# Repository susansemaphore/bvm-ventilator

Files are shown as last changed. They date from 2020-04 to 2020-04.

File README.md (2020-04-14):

# ResQ̇V̇enT Ventilator
An open-source Bag Valve Mask (BVM) based ventilator. Designed to be simple, low cost and robust. The project aims to assist hospitals, by supplementing their existing ventilator fleet in times of high demand such as the COVID-19 outbreak.

## System Diagram
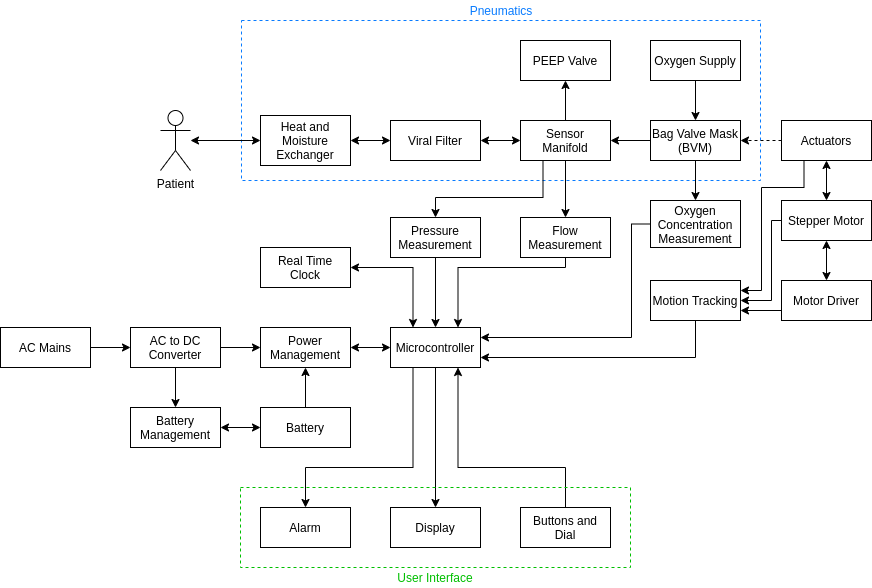
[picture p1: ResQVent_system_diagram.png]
ResQ̇V̇enT System Diagram


## Requirements
### Primary Technical Requirements
* Working pressure at patient: 10 - 40 HPa
* Tidal Volume: 250 - 800 ml
* Respiratory Rate: 10 - 30 cycles/min
* I:E ratio variable between 1:1 - 1:3
* Physical peak pressure relief: Fixed at 40 HPa
* Adjustable PEEP pressure
* All adjustable parameters should be adjustable without interrupting operation
* Infection control
  * All components that come into contact with the patient’s breath need to be easily cleaned or disposable
  * The working pressure should accommodate the use of a HMEF-bacterial-viral filter
* Reliability: 100% duty cycle for 14 days
* Safety: The device should not pose any risk to the patient or healthcare workers
* Mode of operation: Mandatory Ventilation - Fixed timing parameters with no external breath triggers

### Secondary Technical Requirements
* Mode of operation: Pressure support - The patient initiates a breath which is supported by the machine.
* Accommodation for an ultrasonic humidifier-warmer
* Battery backup - the minimum period of which needs to comfortably span the time it may take for a backup generator to kick in. However longer term operation would be ideal

### User Requirements
* The device as a whole needs to be easily cleanable
* Information display needs to be clear
* User interaction needs to be obvious and in metrics commonly understood by doctors
* User manual to be simple 1 pager
* The BVM should be easily replaceable and the machine's recalibration should be simple

### Other Requirements
* Cost: As low as possible. But being a medical device, robustness and feature completion is the primary goal.

## Requirements source documents
* [SASA Ventilator Requirements](https://drive.google.com/file/d/1E5HM6Y5oINCTi7c1G11EO2v6UM-miFut/view?usp=sharing)
* [UK Government Ventilator Requirements ](https://www.gov.uk/government/publications/coronavirus-covid-19-ventilator-supply-specification/rapidly-manufactured-ventilator-system-specification)
* [Open source requirements](https://docs.google.com/document/d/1FNPwrQjB1qW1330s5-S_-VB0vDHajMWKieJRjINCNeE/edit?fbclid=IwAR3ugu1SGMsacwKi6ycAKJFOMduInSO4WVM8rgmC4CgMJY6cKaGBNR14mpM)

## Similar Projects
* [OpenLung](https://gitlab.com/TrevorSmale/OSV-OpenLung/-/tree/master)
* [Open Source Covid-19 Ventilator Canada](https://open-source-covid-19-ventilator-canada.mn.co/)
* [E-Vent - MIT](https://e-vent.mit.edu/)
* [COVID-19 Project: Rapidly Manufactured Medical Equipment - OfferZen](https://www.offerzen.com/blog/covid-19-project-rapidly-manufactured-medical-equipment)
* [ApolloBVM by Take a Breather - Rice University](https://news.rice.edu/2020/03/27/ventilator-costing-less-than-300-developed-by-rice-university-and-metric-technologies/)
* [Ambovent](https://github.com/AmboVent/AmboVent)

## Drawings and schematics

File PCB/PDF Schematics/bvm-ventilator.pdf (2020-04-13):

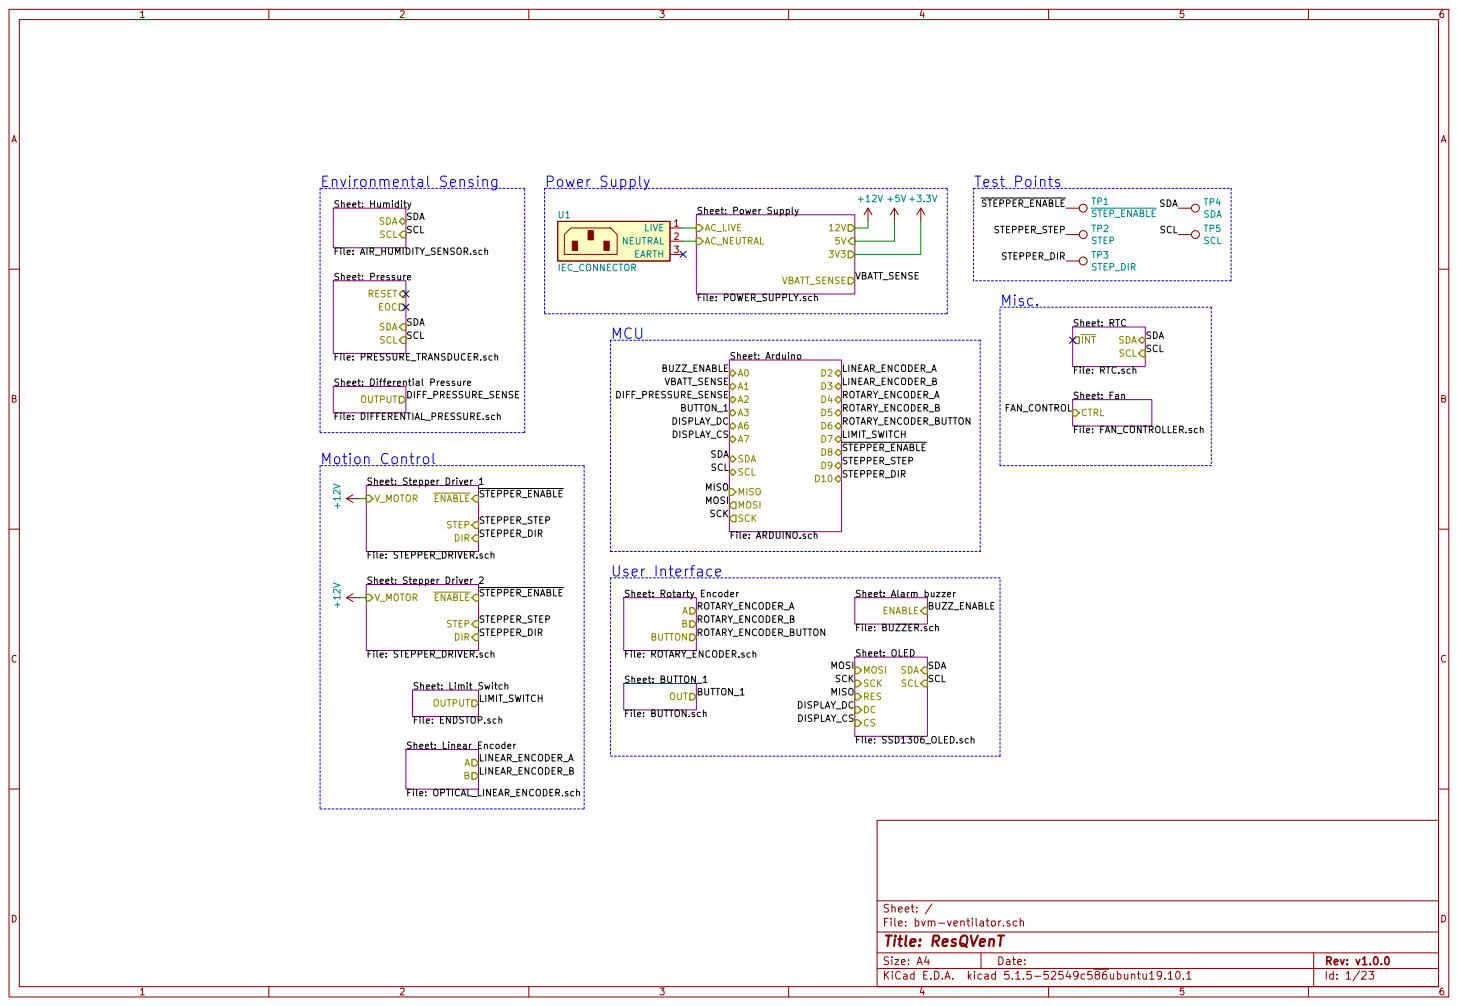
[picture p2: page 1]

TP1 STEP_ENABLE +12V
Sheet: Humidity File: AIR_HUMIDITY_SENSOR.sch SDA

Sheet: Fan File: FAN_CONTROLLER.sch CTRL +12V

INT Sheet: Power Supply File: POWER_SUPPLY.sch AC_LIVE

IEC_CONNECTOR +12V
Sheet: Pressure File: PRESSURE_TRANSDUCER.sch RESET EOC

DISPLAY_DC
DISPLAY_CS MISO MOSI SCK
SCL SDA ROTARY_ENCODER_B
SCL MISO MOSI SCK

Sheet: Stepper Driver 1 File: STEPPER_DRIVER.sch V_MOTOR

Sheet: Stepper Driver 2 File: STEPPER_DRIVER.sch V_MOTOR

Sheet: BUTTON_1 File: BUTTON.sch OUT Sheet: Rotarty Encoder File: ROTARY_ENCODER.sch A

Sheet: Alarm buzzer File: BUZZER.sch ENABLE

Sheet: Linear Encoder File: OPTICAL_LINEAR_ENCODER.sch A

File: bvm-ventilator.sch Sheet: /
Id: 1/23 Title: ResQVenT

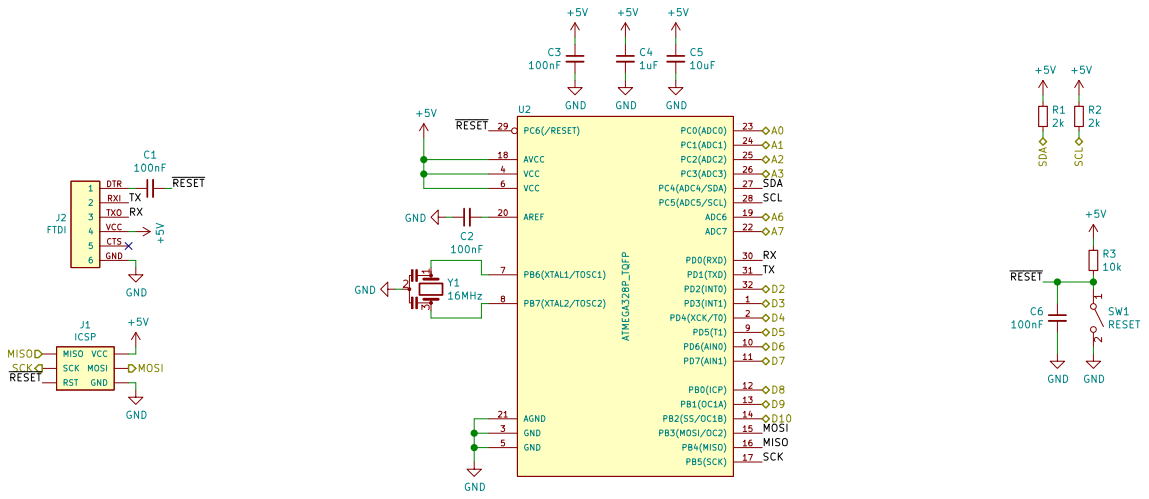
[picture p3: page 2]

File: ARDUINO.sch Sheet: /Arduino/
Id: 2/23 Title: ResQVenT

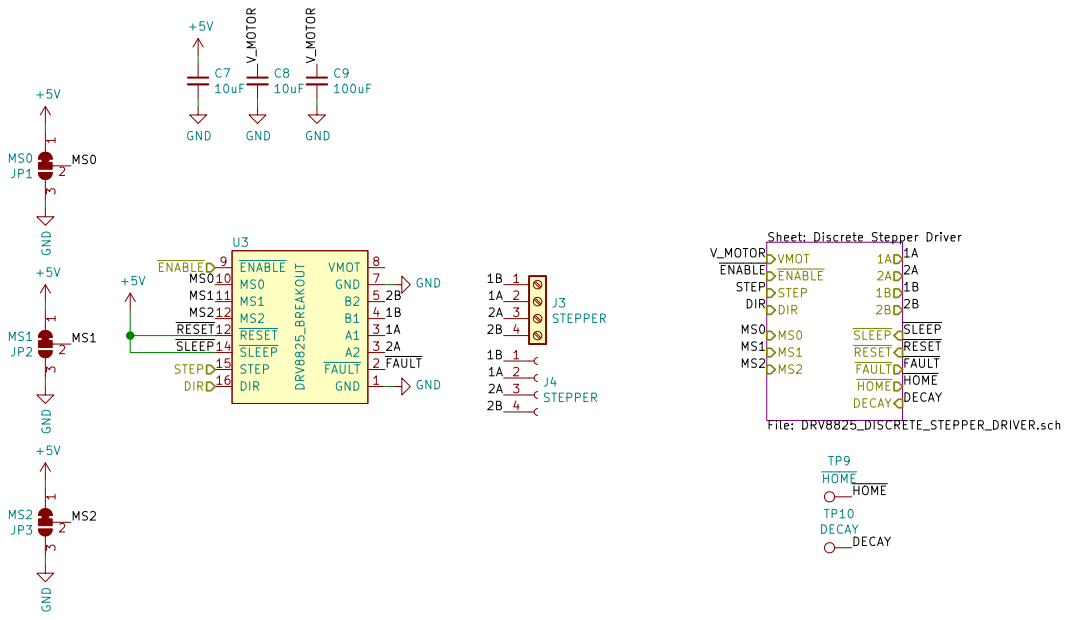
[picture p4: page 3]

FAULT HOME DECAY GND GND

Sheet: Discrete Stepper Driver File: DRV8825_DISCRETE_STEPPER_DRIVER.sch

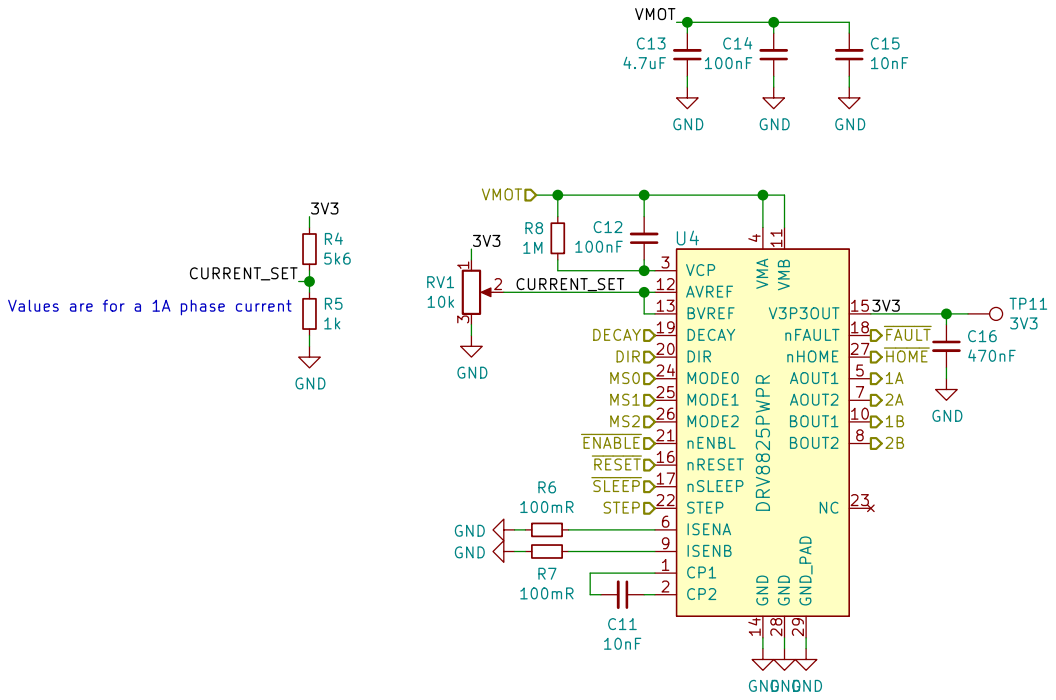
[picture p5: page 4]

3V3 CURRENT_SET Values are for a 1A phase current

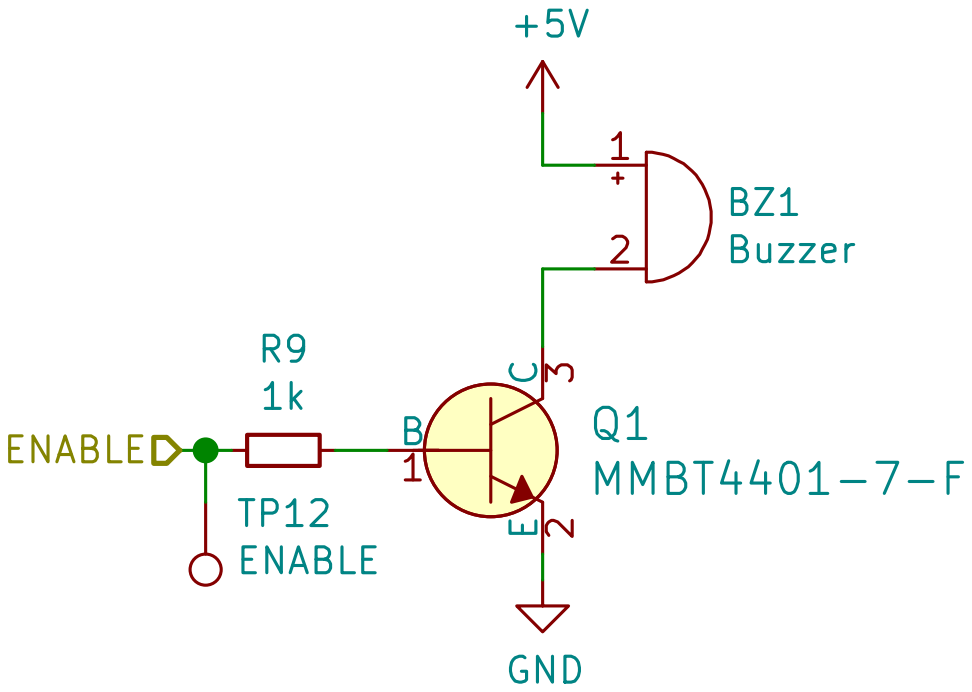
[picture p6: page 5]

File: BUZZER.sch Sheet: /Alarm buzzer/ B

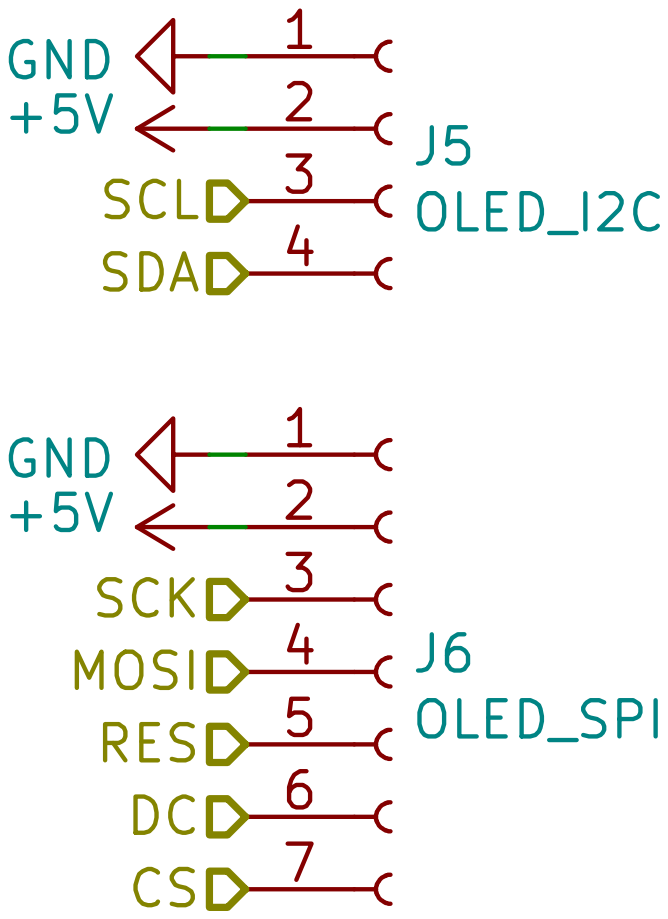
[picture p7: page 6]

File: SSD1306_OLED.sch Sheet: /OLED/ GND
J6OLED_SPI +5V

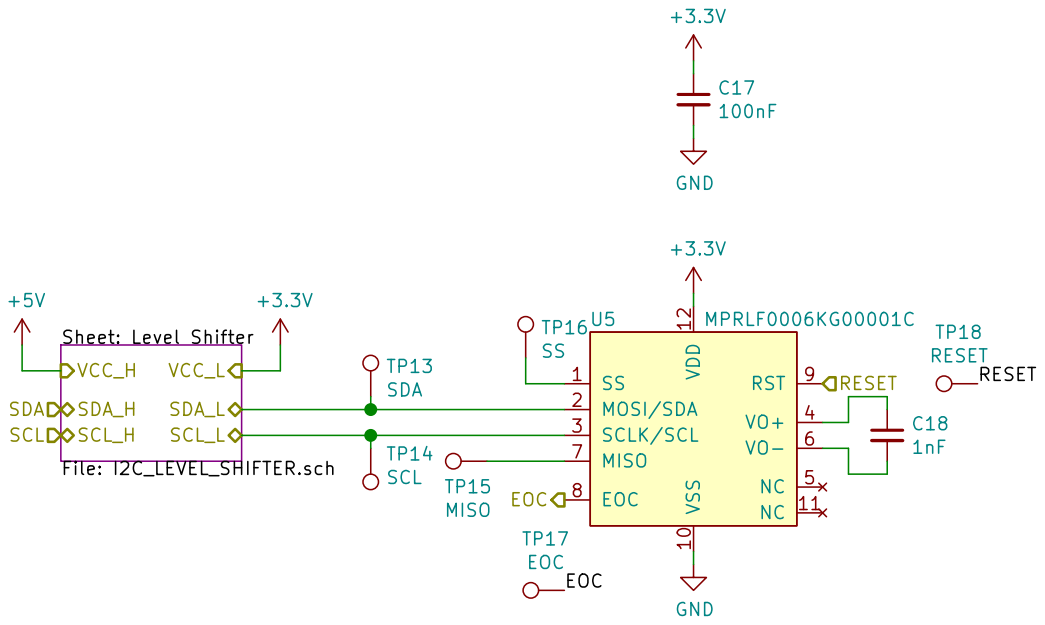
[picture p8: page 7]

TP14 SCL +5V
Sheet: Level Shifter File: I2C_LEVEL_SHIFTER.sch SDA_L SCL_L SDA_H

File: PRESSURE_TRANSDUCER.sch Sheet: /Pressure/
Id: 7/23 Title: ResQVenT

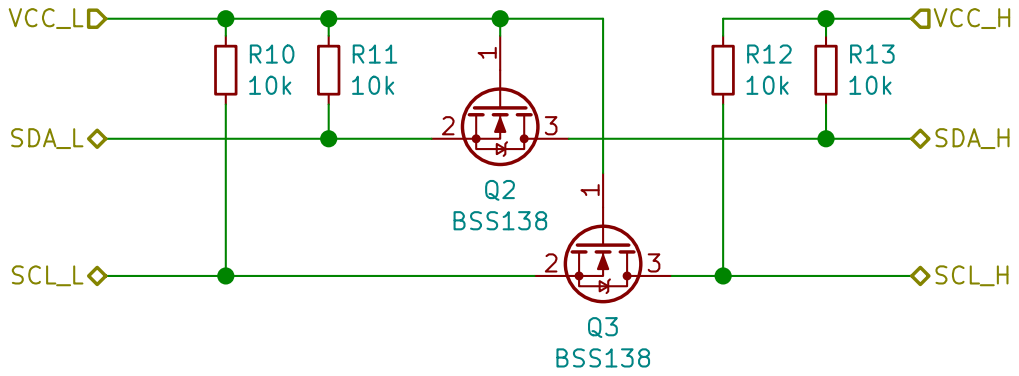
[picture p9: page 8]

File: I2C_LEVEL_SHIFTER.sch Sheet: /Pressure/Level Shifter/
Id: 8/23 Title: ResQVenT

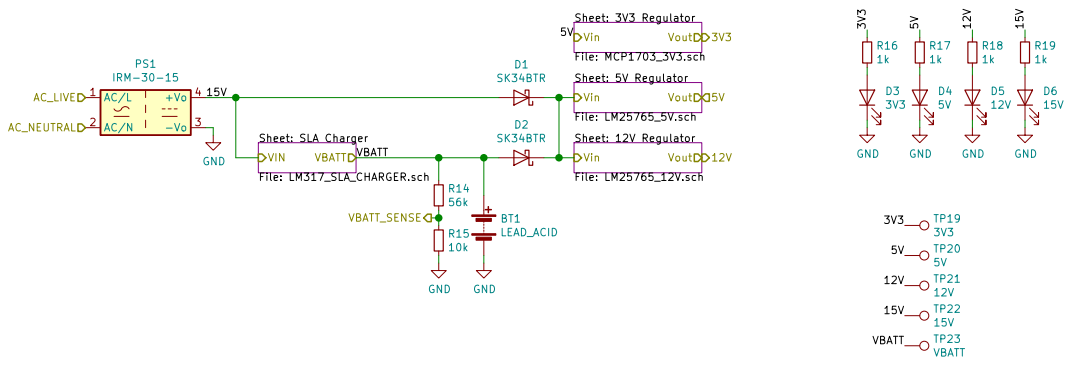
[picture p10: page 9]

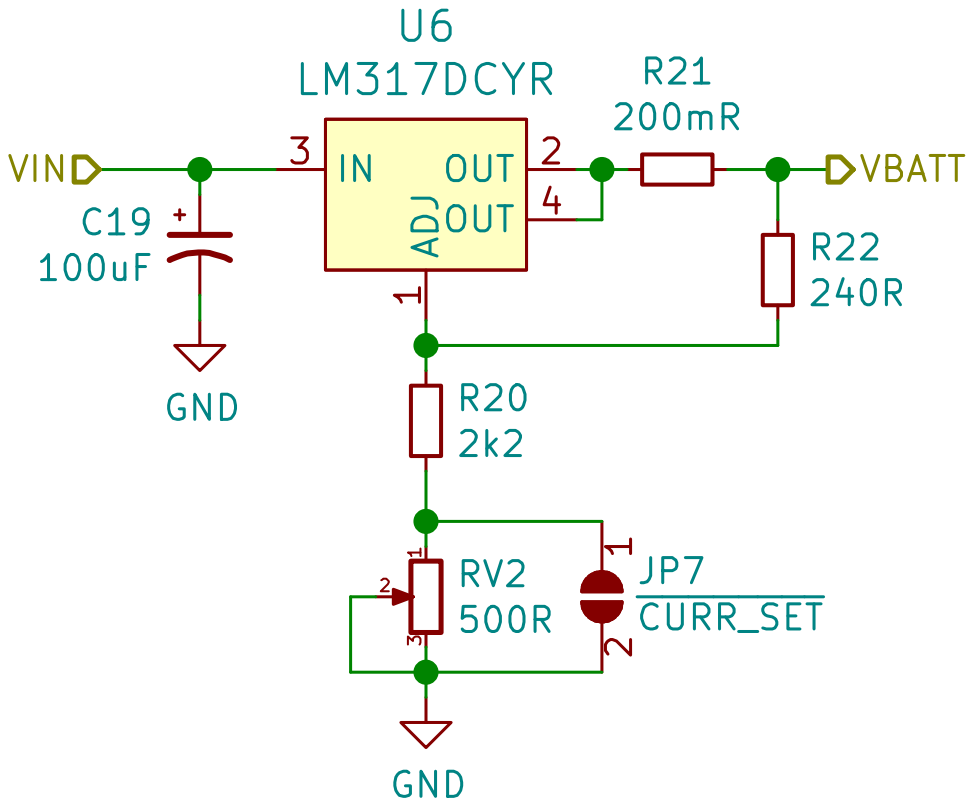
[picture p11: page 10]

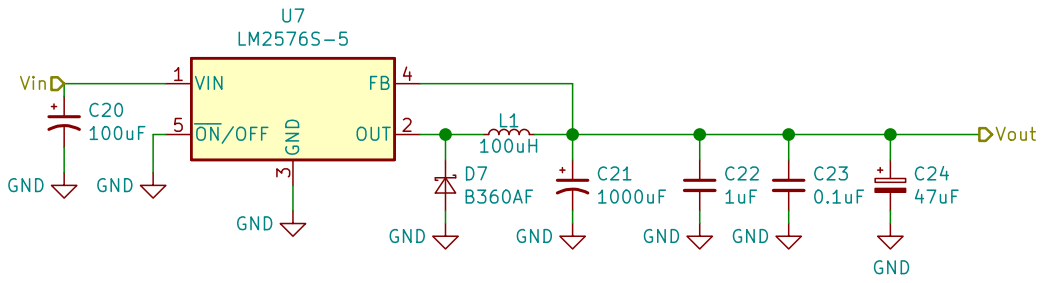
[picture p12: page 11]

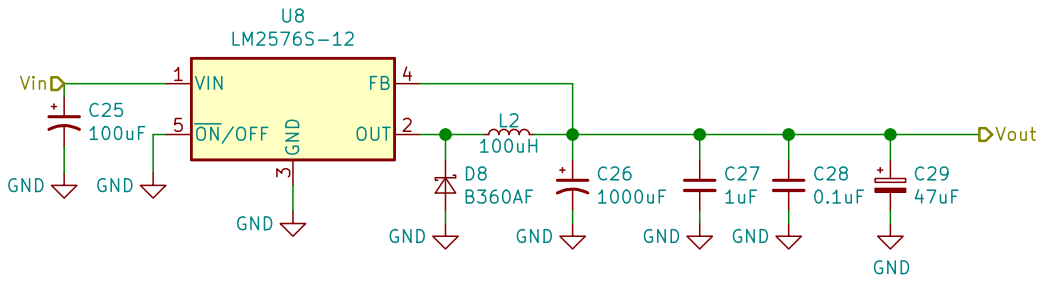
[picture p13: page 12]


1 VO 2 VI 3 U9 MCP1703A-3302_SOT23 Vin Vout

Sheet: /Power Supply/3V3 Regulator/ C30


FAULT HOME DECAY GND GND

Sheet: Discrete Stepper Driver File: DRV8825_DISCRETE_STEPPER_DRIVER.sch


3V3 CURRENT_SET Values are for a 1A phase current


File: RTC.sch Sheet: /RTC/ BT2 C2032 +5V


File: ENDSTOP.sch Sheet: /Limit Switch/
Id: 17/23 Title: ResQVenT



File: BUTTON.sch Sheet: /BUTTON_1/
Id: 19/23 Title: ResQVenT


File: OPTICAL_LINEAR_ENCODER.sch Sheet: /Linear Encoder/
Id: 20/23 Title: ResQVenT



File: DIFFERENTIAL_PRESSURE.sch Sheet: /Differential Pressure/
Id: 22/23 Title: ResQVenT


File: FAN_CONTROLLER.sch Sheet: /Fan/
Id: 23/23 Title: ResQVenT

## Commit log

2020-03-30 Added similar projects and source material
2020-03-30 Added PCB project files
    [bvm-ventilator.kicad_pcb, bvm-ventilator.sch]
2020-03-31 Filled out page setup
    [bvm-ventilator.sch]
2020-03-31 Added basic Arduino schematic
    [bvm-ventilator.sch]
2020-03-31 Moved Arduino into subsheet
    [ARDUINO.sch, bvm-ventilator.sch]
2020-03-31 Added stepper driver module and AC/DC
    [ARDUINO.sch, STEPPER_DRIVER.sch, bvm-ventilator.sch]
2020-04-01 Finished stepper driver
    [STEPPER_DRIVER.sch, bvm-ventilator.sch]
2020-04-01 Added additional decoupling to stepper driver
    [STEPPER_DRIVER.sch]
2020-04-01 Added Loadcell amplifier
    [ARDUINO.sch, HX711_LOADCELL_AMP.sch, STEPPER_DRIVER.sch, bvm-ventilator.sch]
2020-04-01 complete loadcell connector
    [HX711_LOADCELL_AMP.sch]
2020-04-01 Added buzzer
    [ARDUINO.sch, BUZZER.sch, HX711_LOADCELL_AMP.sch, STEPPER_DRIVER.sch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]
2020-04-01 Added pot, OLED and LCD sheets
    The displays have not yet been populated
    [ARDUINO.sch, BUZZER.sch, HD44780_LCD.sch, HX711_LOADCELL_AMP.sch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]
2020-04-02 Filled LCD and OLED
    [ARDUINO.sch, BUZZER.sch, HD44780_LCD.sch, HX711_LOADCELL_AMP.sch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]
2020-04-02 Added pressure sensor
    [PRESSURE_TRANSDUCER.sch, bvm-ventilator.sch]
2020-04-02 Added button
    [ARDUINO.sch, BUTTON.sch, BUZZER.sch, HD44780_LCD.sch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]
2020-04-02 Added pressure sensor datasheet
    [POWER_SUPPLY.sch, PRESSURE_TRANSDUCER.sch, bvm-ventilator.sch]
2020-04-02 Added second stepper driver and empty PSU
    [STEPPER_DRIVER.sch, bvm-ventilator.sch]
2020-04-03 Added RTC
    [ARDUINO.sch, BUTTON.sch, BUZZER.sch, HD44780_LCD.sch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]
2020-04-04 Added Endstop and AMUX
    Also started connecting things to get an idea of pin usage
    [ANALOG_MUX.sch, ARDUINO.sch, BUTTON.sch, BUZZER.sch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]
2020-04-04 Replaced Pots with Encoder
    [ANALOG_MUX.sch, ARDUINO.sch, BUTTON.sch, BUZZER.sch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]
2020-04-04 Swapped sleep for enable pin on stepper driver
    [ANALOG_MUX.sch, ARDUINO.sch, BUTTON.sch, BUZZER.sch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]
2020-04-05 Added discrete stepper drivers
    I will route both so that either modules or discrete modules can be used
    [ANALOG_MUX.sch, ARDUINO.sch, BUTTON.sch, BUZZER.sch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]
2020-04-05 Added 12V regulator
    [ANALOG_MUX.sch, ARDUINO.sch, BUTTON.sch, BUZZER.sch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]
2020-04-06 Removed Loadcell
    We don't need it
    [ANALOG_MUX.sch, ARDUINO.sch, BUTTON.sch, BUZZER.sch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]
2020-04-06 Started thinking through power supply
    [ANALOG_MUX.sch, ARDUINO.sch, BUTTON.sch, BUZZER.sch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]
2020-04-06 Simplified power supply
    [LTC4079F_MULTI_CHARGER.sch, POWER_SUPPLY.sch]
2020-04-06 Added battery voltage sense
    [LM25765.sch, POWER_SUPPLY.sch, bvm-ventilator.sch]
2020-04-06 Added LM317 SLA charger
    [LM317_SLA_CHARGER.sch, POWER_SUPPLY.sch]
2020-04-06 Updated power mixing
    [POWER_SUPPLY.sch]
2020-04-06 Added 3V3 regulator
    [ANALOG_MUX.sch, ARDUINO.sch, BUTTON.sch, BUZZER.sch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]
2020-04-06 Removed Analog MUX
    [ARDUINO.sch, BUTTON.sch, BUZZER.sch, DRV8825_DISCRETE_STEPPER_DRIVER.sch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]
2020-04-06 Hooked up 3v3 regulator
    [bvm-ventilator.sch]
2020-04-06 Added Power LEDs
    [LM25765_12V.sch, POWER_SUPPLY.sch]
2020-04-06 Added resistors to set stepper motor current
    Once a current is specified the pot can be removed in favor of resistors for production ease
    [DRV8825_DISCRETE_STEPPER_DRIVER.sch, STEPPER_DRIVER.sch]
2020-04-06 Added additional power LED
    [POWER_SUPPLY.sch]
2020-04-07 Removed DK additional fields
    [BUZZER.sch, DRV8825_DISCRETE_STEPPER_DRIVER.sch, LM317_SLA_CHARGER.sch]
2020-04-07 Annotated Schematic
    [ARDUINO.sch, BUTTON.sch, BUZZER.sch, DRV8825_DISCRETE_STEPPER_DRIVER.sch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]
2020-04-07 Added Dielectric and voltage rating to all capacitors
    [ARDUINO.sch, BUTTON.sch, DRV8825_DISCRETE_STEPPER_DRIVER.sch, ENDSTOP.sch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]
2020-04-07 Named elements with missing values
    [ARDUINO.sch, BUTTON.sch, RTC.sch, STEPPER_DRIVER.sch]
2020-04-07 Added some footprints
    [ARDUINO.sch, BUTTON.sch, POWER_SUPPLY.sch, PRESSURE_TRANSDUCER.sch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]
2020-04-07 Added optical linear encoder
    [ARDUINO.sch, BUTTON.sch, BUZZER.sch, DRV8825_DISCRETE_STEPPER_DRIVER.sch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]
2020-04-08 Added differential pressure and level shifter for gauge pressure sensor
    [AIR_HUMIDITY_SENSOR.sch, ARDUINO.sch, BUTTON.sch, BUZZER.sch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]
2020-04-08 Replaced 3v3 regulator with 5v
    [LM25765_5V.sch, POWER_SUPPLY.sch]
2020-04-08 Increased VCC from 3v3 to 5v
    [AIR_HUMIDITY_SENSOR.sch, ARDUINO.sch, BUTTON.sch, BUZZER.sch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]
2020-04-08 Increased MCU XTAL frequency
    At 5V it can operate at 16MHz
    [ARDUINO.sch]
2020-04-08 Connected Differential pressure sensor
    [DIFFERENTIAL_PRESSURE.sch, bvm-ventilator.sch]
2020-04-08 Added Humidity and temperature sensors
    [AIR_HUMIDITY_SENSOR.sch, ARDUINO.sch, BUTTON.sch, BUZZER.sch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]
2020-04-08 Added HIH712x datasheet
    [AIR_HUMIDITY_SENSOR.sch]
2020-04-08 Reconnected Button pins
    [bvm-ventilator.sch]
2020-04-08 Added SPI OLED display
    the I2C bus is pretty bloated and will be slow to update
    [AIR_HUMIDITY_SENSOR.sch, ARDUINO.sch, BUTTON.sch, BUZZER.sch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]
2020-04-08 Added IEC connector and organised
    [BUTTON.sch, DRV8825_DISCRETE_STEPPER_DRIVER.sch, MCP1703_3V3.sch, SSD1306_OLED.sch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]
2020-04-09 Moved submodules into PCB subdirectory
    [DRV8825_DISCRETE_STEPPER_DRIVER.sch, STEPPER_DRIVER.sch, bvm-ventilator.sch]
2020-04-10 Swapped crystal for resonator
    [ARDUINO.sch, DRV8825_DISCRETE_STEPPER_DRIVER.sch, STEPPER_DRIVER.sch]
2020-04-10 Added solder jumpers to MS pins on stepper drivers
    This will let us choose the microstepping options
    [DRV8825_DISCRETE_STEPPER_DRIVER.sch, STEPPER_DRIVER.sch]
2020-04-10 Added test points to sensors
    [AIR_HUMIDITY_SENSOR.sch, DIFFERENTIAL_PRESSURE.sch, PRESSURE_TRANSDUCER.sch, bvm-ventilator.sch]
2020-04-10 Added correct DRV breakout and added testpoints
    [DIFFERENTIAL_PRESSURE.sch, DRV8825_DISCRETE_STEPPER_DRIVER.sch, PRESSURE_TRANSDUCER.sch, RTC.sch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]
2020-04-10 Added test points to PSU
    [OPTICAL_LINEAR_ENCODER.sch, POWER_SUPPLY.sch, STEPPER_DRIVER.sch, bvm-ventilator.sch]
2020-04-10 Added remaining test points
    [AIR_HUMIDITY_SENSOR.sch, ARDUINO.sch, BUTTON.sch, BUZZER.sch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]
2020-04-10 Added breakout footprints
    [DRV8825_DISCRETE_STEPPER_DRIVER.sch, STEPPER_DRIVER.sch]
2020-04-10 Removed unneeded test points
    [STEPPER_DRIVER.sch]
2020-04-10 Added RV bypass jumper to SLA charger
    In production this can be jumped and the current set resistor pair adjusted in order to remove the need for the pot
    [DRV8825_DISCRETE_STEPPER_DRIVER.sch, LM317_SLA_CHARGER.sch]
2020-04-10 Added PDF schematic
    [DRV8825_DISCRETE_STEPPER_DRIVER.sch, LM317_SLA_CHARGER.sch, STEPPER_DRIVER.sch]
2020-04-11 Added CR2032 holder footprint
    [RTC.sch]
2020-04-11 Swapped MSx jumpers around so that fullstep is default
    The footprint used defaults to bridging pins 2 and 3
    [ARDUINO.sch, BUZZER.sch, SSD1306_OLED.sch, STEPPER_DRIVER.sch]
2020-04-11 Added majority footprints
    [AIR_HUMIDITY_SENSOR.sch, ARDUINO.sch, BUTTON.sch, BUZZER.sch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]
2020-04-11 Added more footprints
    [ARDUINO.sch, DIFFERENTIAL_PRESSURE.sch, DRV8825_DISCRETE_STEPPER_DRIVER.sch, LM317_SLA_CHARGER.sch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]
2020-04-12 Replaced Tant Caps with Alu
    [DRV8825_DISCRETE_STEPPER_DRIVER.sch, STEPPER_DRIVER.sch, bvm-ventilator.sch]
2020-04-12 Added correct Alu cap MPNs
    [DRV8825_DISCRETE_STEPPER_DRIVER.sch, LM25765_12V.sch, LM25765_5V.sch, LM317_SLA_CHARGER.sch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]
2020-04-12 Added Rotary encoder MPN and datasheet
    [DRV8825_DISCRETE_STEPPER_DRIVER.sch, ROTARY_ENCODER.sch]
2020-04-13 Added 12v Fan
    [AIR_HUMIDITY_SENSOR.sch, ARDUINO.sch, BUTTON.sch, BUZZER.sch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]
2020-04-13 Added fan driver footprints
    [FAN_CONTROLLER.sch]
